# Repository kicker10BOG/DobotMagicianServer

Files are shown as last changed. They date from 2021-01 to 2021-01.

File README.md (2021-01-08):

# DobotMagicianServer
A web server for controlling a Dobot Magician robotic arm

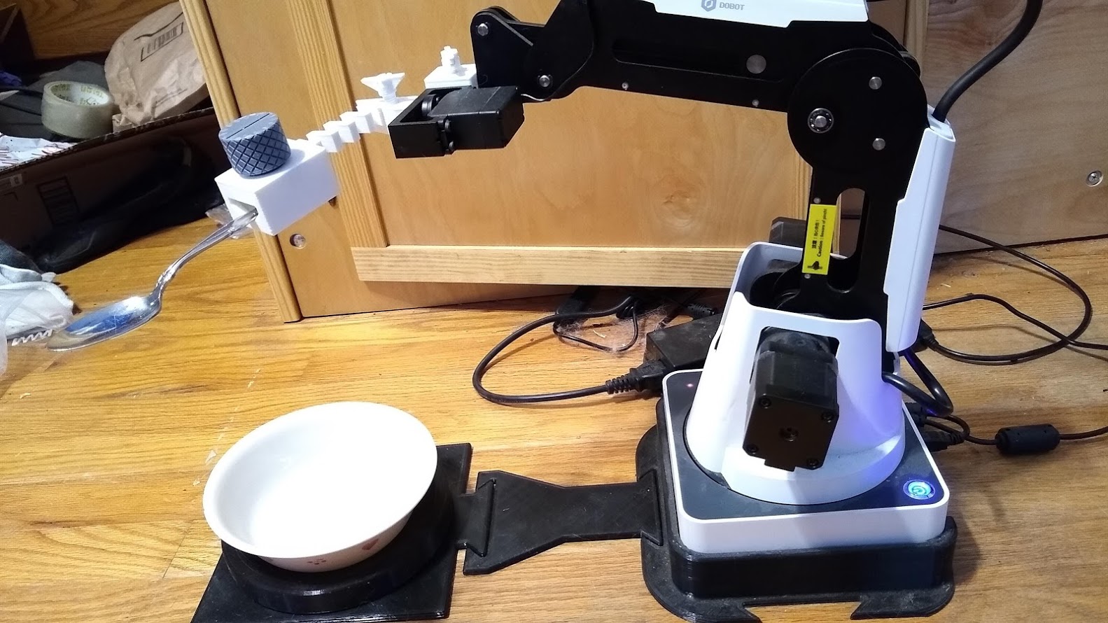
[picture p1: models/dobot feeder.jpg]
Picture of 3d prints on dobot magician


## Why

I needed to replace my 20+ year old machine and all of the specialized devices were just too expensive, so I got a Dobot Magician because it's much less expensive and more versatile than any of the specialized devices. Being in software development, I knew I could write code to make it work how I wanted. And being decent with Fusion 360 made me confident I could design the necessary models. 

Video of how it works: 

IMAGE ALT TEXT HERE (https://www.youtube.com/watch?v=Gtf_Rhcddrw)

The video shows a pi zero w, but I'm using a pi 3b+ now as I think there's something in the code I need to fix so it works more reliably over longer periods of time. Right now the Dobot service I setup needs to be restarted every so often or it stops serving and the 3b+ handles that much better than the zero w. I'm pretty sure that issue is fixed now.

Feel free to take the models and code and modify them for anything you need. I want this to be easily accessible an modifiable by anyone who needs it. I'm including the f3d and step files to make that easier.

I want to thank luismesas for creating the pydobot project. It made getting this to work much easier. I use a modified version of his library. You can find that project at https://github.com/luismesas/pydobot

## What You Need
The following are necessary for this to work right. 

* Dobot Magician (Note: I have only tested this on the Magician, not the Magician Lite and my research shows that it will need quite a few modifications to work with the Lite)
* A 3d-printer or access to a 3d-printer. I used an Ender 3. 
* A Raspberry Pi you can leave connected to the Dobot. I use a Raspberry Pi 3b+
* USB-A to USB-B cable (and a USB-A to micro USB adapter if using a Pi Zero W)

## Hardware Setup
3d-Print the following models from the models directory. I printed everything in PLA, so I don't know if other materials will require design changes, particularly for the spring. If anything does require a change to the design, the f4d and step files are included. Every model can be oriented to print without support. 

* 90 degree bracket.stl
* adapter acrew.stl
* utensil holder.stl
* utensil screw.stl
* mount screw.stl
* base.stl
* spacer.stl
* bowl panel.stl
* bowl disc.stl

Place the Dobot in the base with the ports visible over the short portion of the base. 
Attach the spacer to the base on the opposite side of the ports. 
Attach the bowl panel to the other end of the spacer and put the bowl disc on top of it. 

The Dobot comes with several toolheads and one of them should have a servo motor attached to it. Detach the servo. 
Take the 90 degree bracket and attach it to the dobot. Tighten the thumb screw on the bottom of where it attaches.
Attach the servo to the 90 degree bracket and use the adapter screw to keep it in place. 
Attach the the utensil holder to the servo motor, making sure the flat portion of the shaft faces the screw hole on the utensil holder, then use to the mount screw to help keep it in place. 
Screw the untensil screw in some. 

Now it's ready to have a spoon in the utensil holder and a bowl on the bowl disc and it should like the picture at the top except the arm won't stay up like that while powered off. 

Plug it into power and use the USB cable to connect it to the Raspberry Pi. Plug the Pi into power. 

## Software Setup 
Follow this guide to initally setup the Pi if you don't want to attach a monitor, keyboard, and mouse to it. https://www.tomshardware.com/reviews/raspberry-pi-headless-setup-how-to,6028.html 

If you don't mind connecting the monitor, keyboard, and mouse to it, this guide is comprehensive. https://projects.raspberrypi.org/en/projects/raspberry-pi-setting-up 

If you set it up without the monitor, keyboard, and mouse, connect to it using SSH. Otherwise, open a terminal on it. 

Install git with the following command

```sudo apt install git``` 

Use git to clone this repository. 

```git clone https://github.com/kicker10BOG/DobotMagicianServer.git```

Install Python 3

```sudo apt install python3```

### Dependencies
You're going to need to use pip to install the following libraries:

* cherrypy
* ws4py
* pyserial
* jinja2

```pip3 install cherrypy ws4py pyserial jinja2```

That should be it for dependencies, but it's been a while since I set it up. If you see something else that needs to go here, create an issue. 

### Running as a service
Then I suggest using a service to keep it running. Below is the service config I use at `/etc/systemd/system/dobot.service`.

```
[Unit]
Description=Dobot Magacian Server
After=network.target
StartLimitIntervalSec=0

[Service]
Type=simple
Restart=always
RestartSec=1
User=pi
WorkingDirectory=/home/pi/DobotMagicianServer
ExecStart=/usr/bin/python3 DobotServer.py

[Install]
WantedBy=multi-user.target
```

After creating that file and checking to make sure the paths are correct, run the following command to have the systemd discover it. Depending on your user permissions, you may need to use sudo. 

```systemctl daemon-reload```

The next command is optional but will ensure it is always enabled.

```systemctl enable dobot.service```

The next one will start it.

```systemctl start dobot.service```

Now the server should be running on port 8080 (unless you changed that in cherrypy.conf) and accessible from any device on your local network at `<Pi-ip-address>:8080`. Or if you're using a browser on the Pi itself, you can go to `localhost:8080`. 

## Using it
When the Dobot is off, the only option that shows in the port selection is not the Dobot. It likely ends in `AMA` followed by a number. When you turn it on, a second option should show up ending in `USB` followed by a number. Select it and hit `connect`. 
Now everything should be functional. 

It is advised to hit the `Home` button when you first connect each time so that the Dobot can be sure of how it is positioned. 

## How It Works
First, it uses websockets to keep everything synced. This is great if you need to have the ability to control it from more than one device. 

The home page of the server has standard controls for the arm. 

Note that it is important to always home the arm before using it after turning it on. This is especially important when trying to repeat specific movements. 

I've tried to design it so that it's easy to create new addons in the future. This is done by using jinja2 for templating and conf files for specifying what addons to use. Right now the only addon is the spoon addon. 

### Spoon Addon
This addon uses a json file to store profiles for different types of spoons. You can easily swap between profiles in the user interface. I still need to add a way to create, edit, and delete profiles in the browser, but it's possible to do those by editing the json file directly. 

The controls on this addon should be pretty self-explanatory, but essentially there are two types of movement in the controls.

1) Performing a motion
2) Going to a specific position

When performing a motion, it chains two or more positions together. 

* The "lower" motion goes the "back" position then the "down" position. 
* The "scoop" motion goes the "down" position then the "scoop" position. 
* The "lower" motion goes the "scoop" position then the "up" position. 

When gusing the position buttons, the arm just goes straight to that position. 

* The "up" position puts the spoon in a position that should be close to the mouth. 
* The "back" position should put the spoon at the top of the back of the bowl. 
* The "down" position puts the spoon either at the bottom of the bowl or close to it. I have profiles that do both and I switch between them depending on how full the bowl is. 
* The "scoop" position should bring the spoon up just out of the bowl in a level position so nothing falls off (usually).

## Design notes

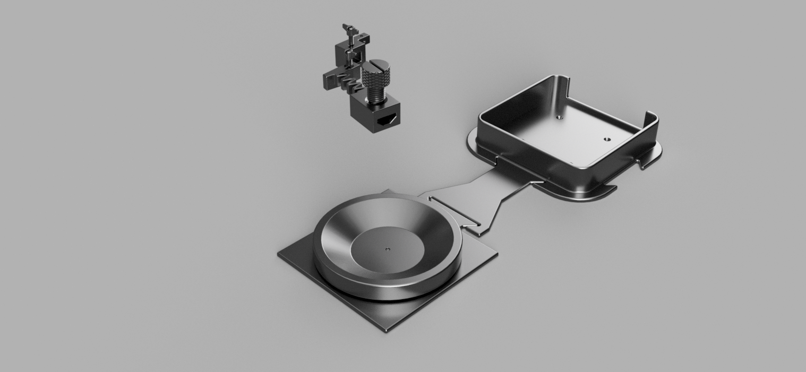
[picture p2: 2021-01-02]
models/feeder.png

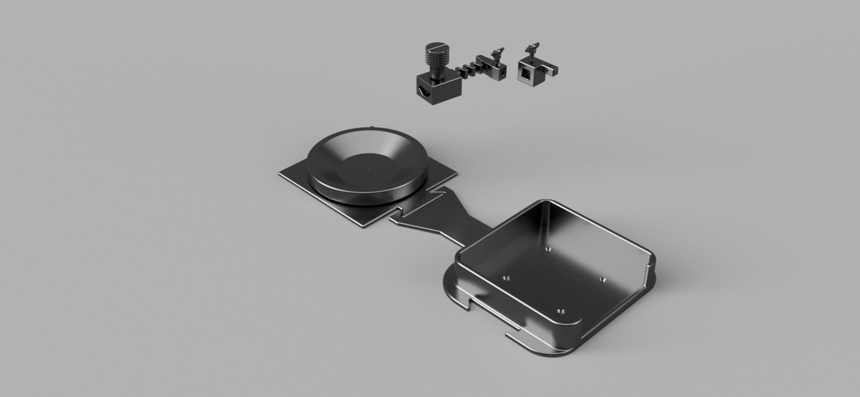
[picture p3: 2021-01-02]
models/feeder - second angle.png

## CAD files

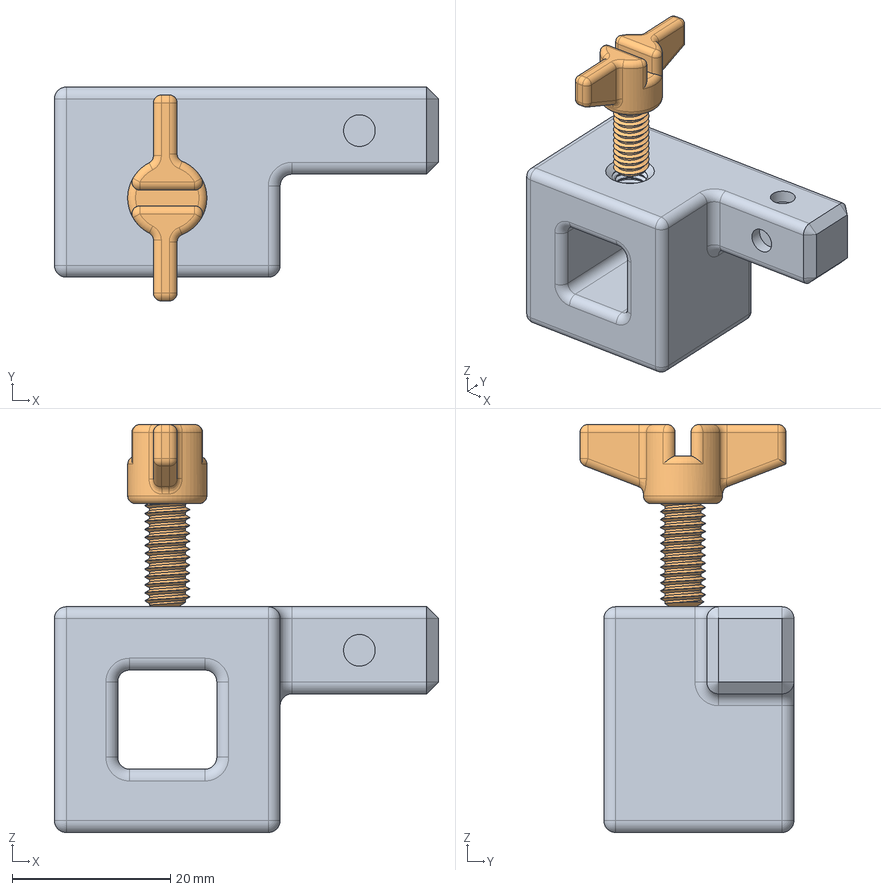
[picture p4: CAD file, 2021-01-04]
models/90 degree adapter.step
48.5 x 27.0 x 51.5 mm

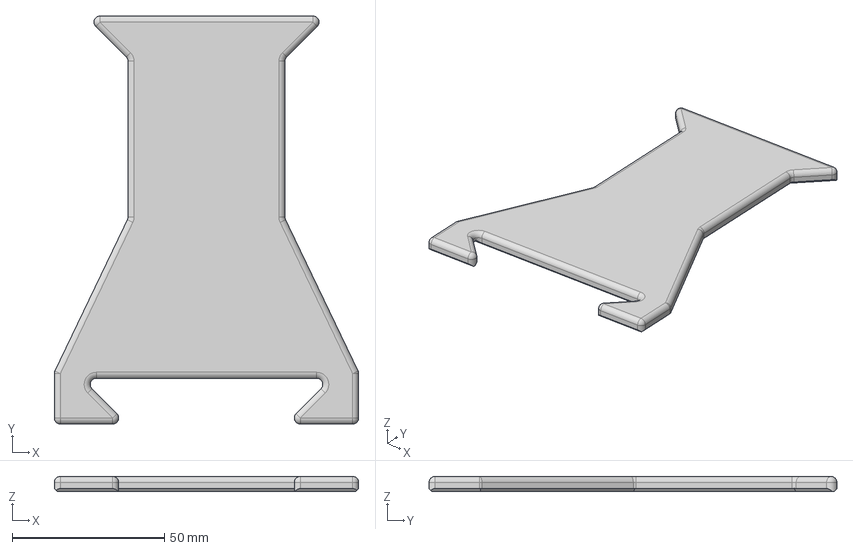
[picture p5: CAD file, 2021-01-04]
models/spacer.step
100.0 x 134.0 x 5.00 mm

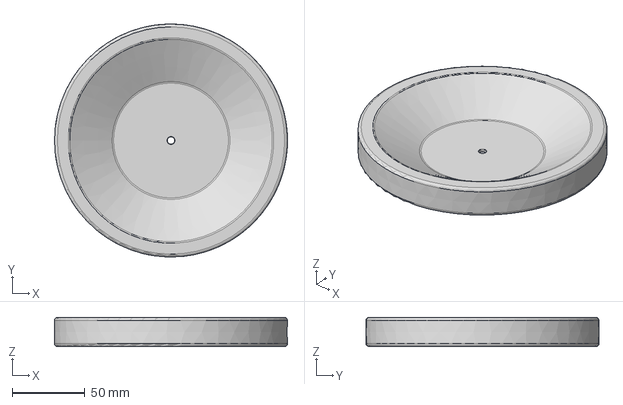
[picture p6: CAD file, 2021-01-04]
models/bowl disc.step
160.0 x 160.0 x 20.0 mm

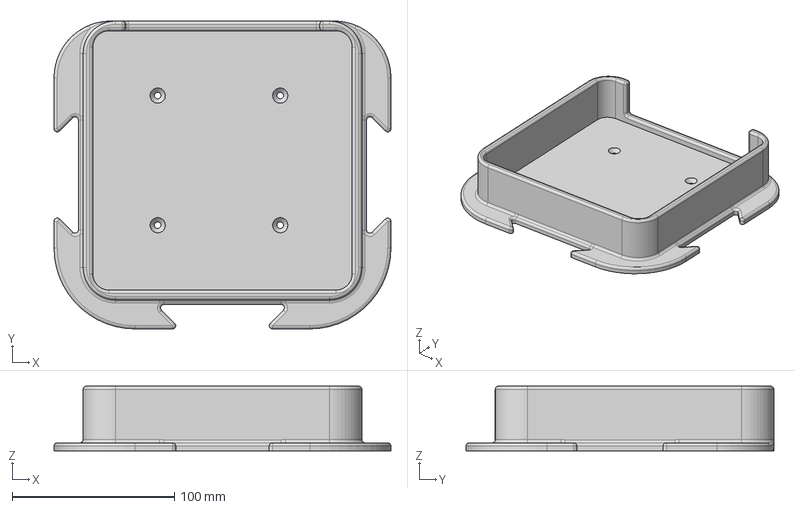
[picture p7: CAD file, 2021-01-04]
models/base.step
208.0 x 190.0 x 40.0 mm

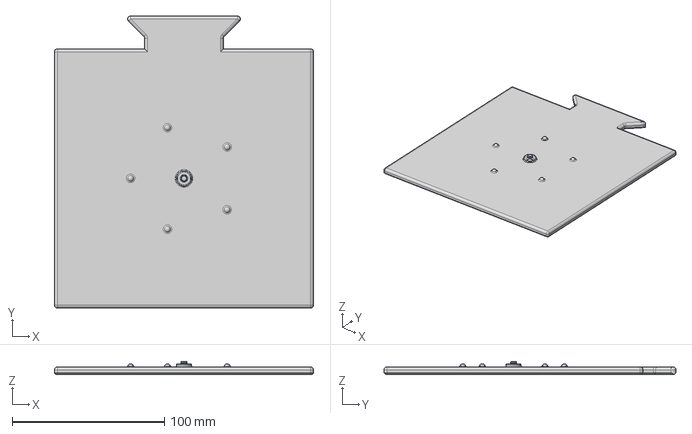
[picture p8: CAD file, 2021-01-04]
models/bowl panel.step
170.0 x 191.5 x 8.50 mm

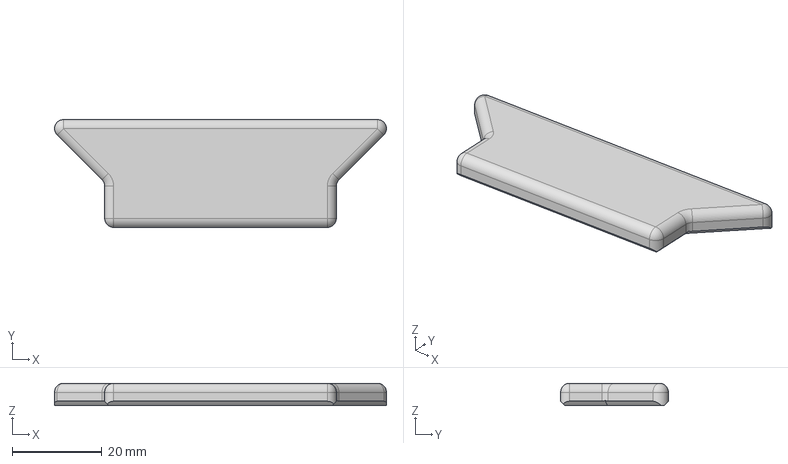
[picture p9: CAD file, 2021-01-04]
models/connect test.step
73.9 x 24.0 x 5.00 mm

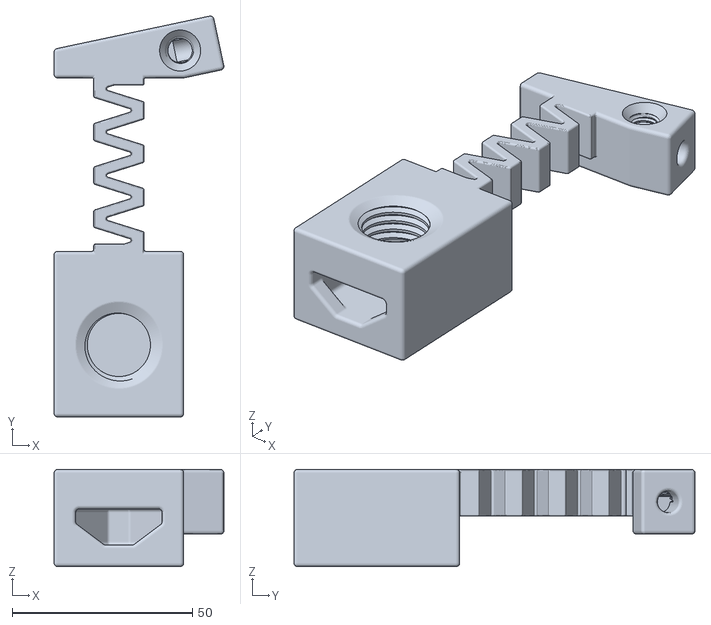
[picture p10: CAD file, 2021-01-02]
models/utensil holder.stl
47.2 x 111.3 x 27.0

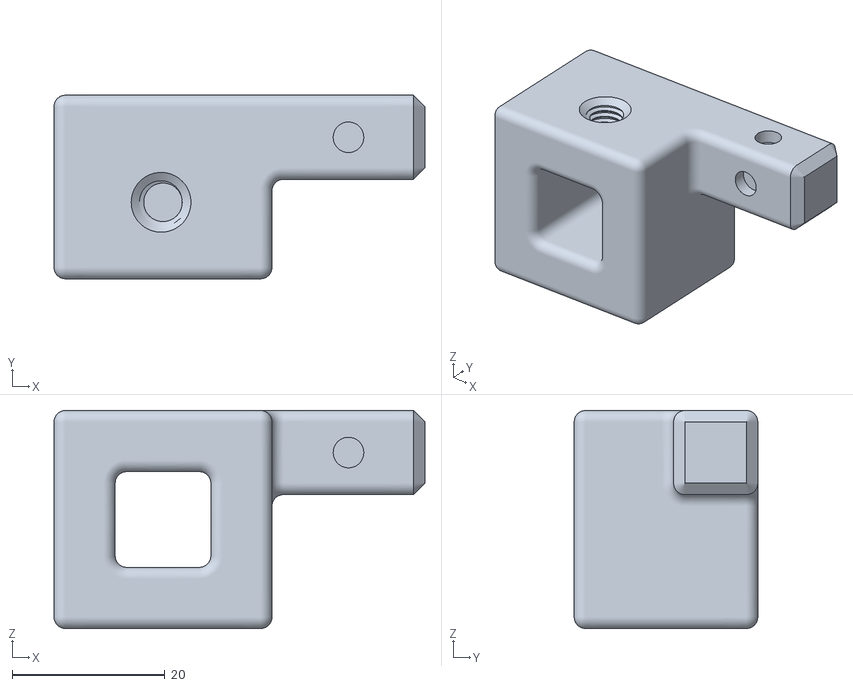
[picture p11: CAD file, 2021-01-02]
models/90 degree bracket.stl
48.5 x 24.0 x 28.5

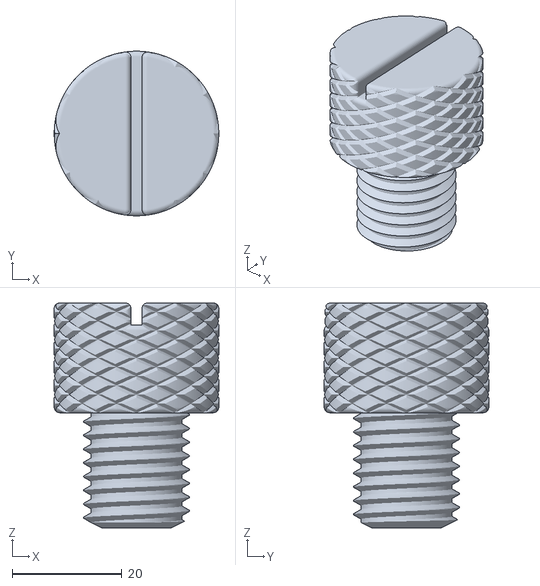
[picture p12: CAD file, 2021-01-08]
models/utensil screw.stl
30.0 x 30.0 x 41.0

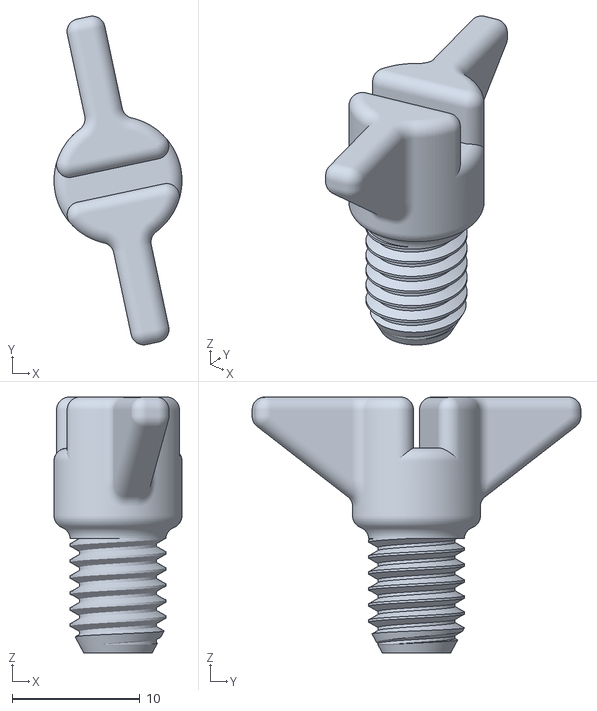
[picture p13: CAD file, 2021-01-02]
models/mount screw.stl
10.00 x 25.7 x 20.0

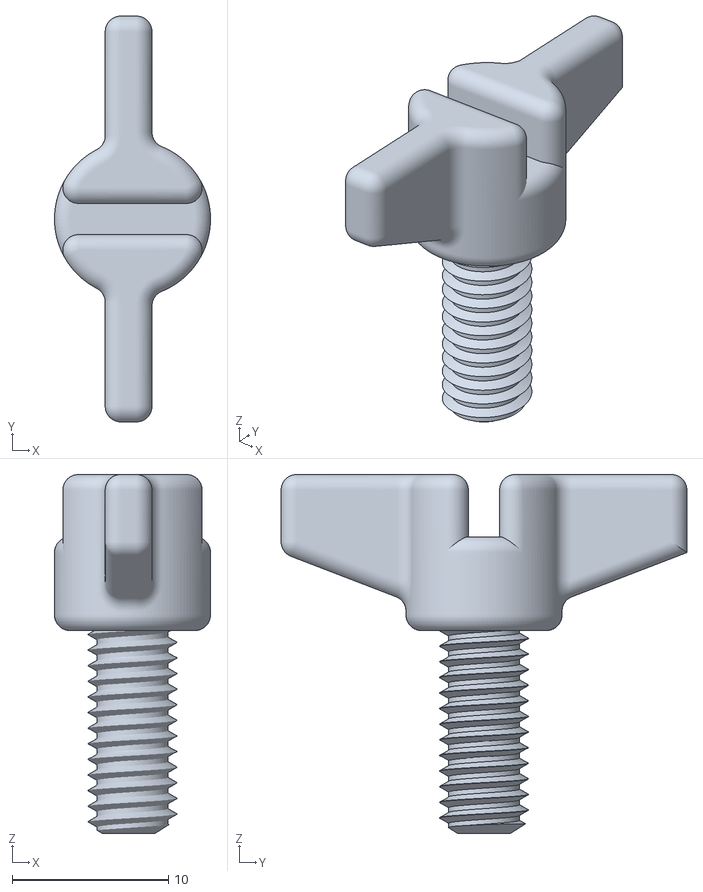
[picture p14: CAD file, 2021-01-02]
models/adapter screw.stl
10.0 x 26.0 x 23.0

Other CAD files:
models/90 degree adapter.f3d
models/base.f3d
models/base.stl
models/bowl disc.f3d
models/bowl disc.stl
models/bowl panel.f3d
models/bowl panel.stl
models/connect test.f3d
models/spacer.f3d
models/spacer.stl
models/utensil holder.f3d

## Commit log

2020-12-31 Update .gitignore
    prep for adding models for 3d printing
2021-01-02 added 3d models
    [90 degree adapter.f3d, 90 degree bracket.stl, Adapter Screw.stl, base.f3d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]
2021-01-02 add spacer f3d file
    [spacer.f3d]
2021-01-04 add step files
    [90 degree adapter.step, base.step, bowl disc.step, bowl panel.step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]
2021-01-08 update models and add more detailed instructions
    [adapter screw.stl, mount screw.stl, utensil screw.stl]
2023-04-22 comment out debug print of ports
